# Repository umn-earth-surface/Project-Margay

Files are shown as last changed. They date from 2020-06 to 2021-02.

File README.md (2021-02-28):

# Project-Margay

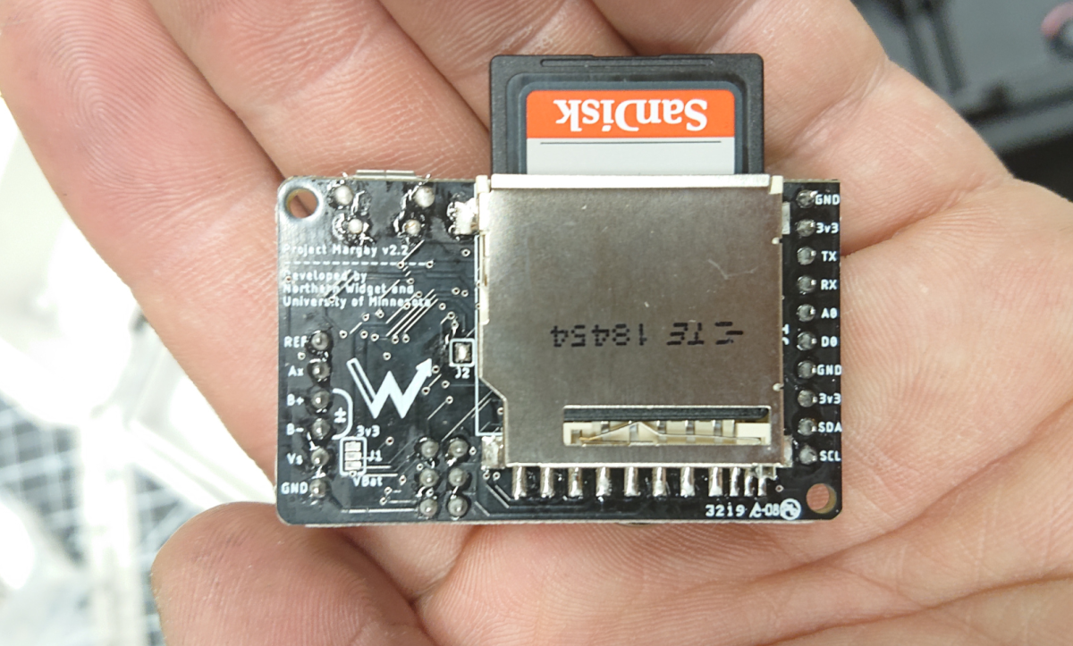
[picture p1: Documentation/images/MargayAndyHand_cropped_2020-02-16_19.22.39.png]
Margay Andy hand Dec 2020


***Margay data logger v2.2.*** *Back side with full-size SD card holder and pinout labels. Standard sized SD card for data storage and scale.*

Project Margay is a micro scale environmental data logger designed based on the ALog series, it is designed to trade IO capabilities for cost and size, allowing for a very simple, but very useful data logger

## Namesake

Due to its small size and adaptability to its environment, Project Margay takes its name from the small Margay cat native to the forests of South and Central America.

>> @awickert: Might be best to add in some feature abilities of the Margay datalogger in part of the namesake to mirror that of the Resnik - let me know what you think the highlights of the logger are and I'll (Josh) put them in

A margay, yawning

##Technical Specifications

>> @awickert: I'm (Josh) drafting up a couple of ways to display the technical specs better, no substantial changes at the moment, but it's next on my list

### Electronic Hardware
This includes a description of the PCB and component functionality

#### Features:
* ATMega644P Processor
* 3.3v Logic
* On board full size SD card (for ease of field use)
* Extremely low sleep current
* Input voltage designed for use with easy to find alkaline batteries
* 0.1" Pitch headers can be populated with header pins and placed on a breadboard for prototyping

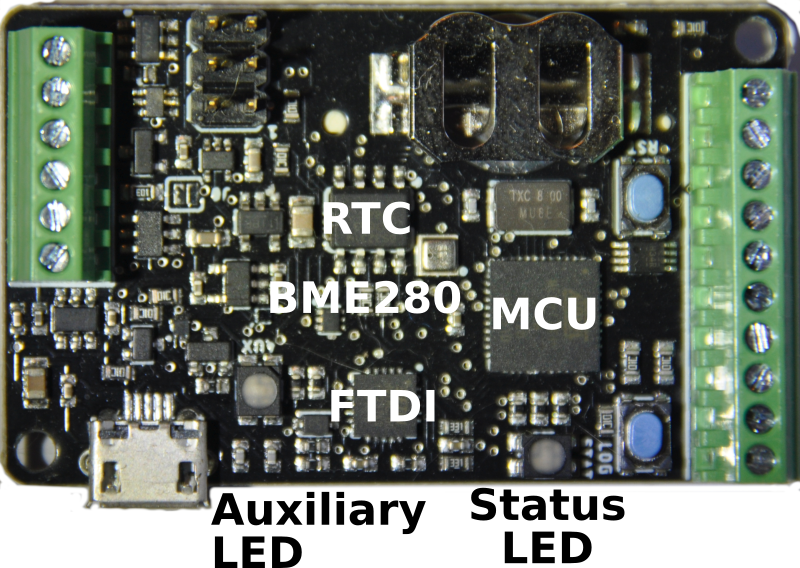
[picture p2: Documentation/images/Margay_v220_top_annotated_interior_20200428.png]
Margay v2.2 interior elements labeled


***Significant components on the Margay v2.2.***

#### v0.0 (Retired)
**Features** <br>
I<sub>Q</sub> = 1.6mA <br>
I<sub>out</sub> = 50mA, max (Regulated power supplied to sensors) <br>
V<sub>in</sub> = 3.3 ~ 5.5v <br>

**IO**:
* 1 I2C Bus
* 1 SPI Bus, with up to 2 CS pins
* 1 PWM Channel (output configurable to 3.3v or VBat via a jumper on bottom of board)
* RGB Status LED
* Auxiliary LED
* Reset Button
* Reconfigurable Button

#### v1.0
**Features** <br>
I<sub>Q</sub> = 2.5&mu;A <br>
I<sub>out</sub> = 50mA, max (Regulated power supplied to sensors) <br>
V<sub>in</sub> = 3.3 ~ 5.5v (Reverse polarity protected) <br>

**IO**
* 1 ADC, 18 bit
* 1 I<sup>2</sup>C Bus
* 1 SPI Bus, with up to 2 CS pins
* 1 PWM Channel (output configurable to 3.3v or VBat via a jumper on bottom of board)
* RGB Status LED
* Auxiliary LED
* Reset Button
* Reconfigurable Button

#### v2.0 (In development)
**Features** <br>
I<sub>Q</sub> = <2.5&mu;A (Estimated) <br>
I<sub>out</sub> = 200mA, max (Regulated power supplied to sensors) <br>
V<sub>in</sub> = 3.3 ~ 5.5v (Reverse polarity protected) <br>

**IO**
* 1 ADC, 18 bit
* 1 I<sup>2</sup>C Bus
* 1 UART Channel
* 2 GPIO Pins (one configurable as an 8 bit ADC)
* 1 PWM Channel (output configurable to 3.3v or VBat via a jumper on bottom of board)
* RGB Status LED
* Auxiliary LED
* Reset Button
* Reconfigurable Button

### Pinout and board interfaces
Pinout is listed on bottom of board, and shown here for v2.2.

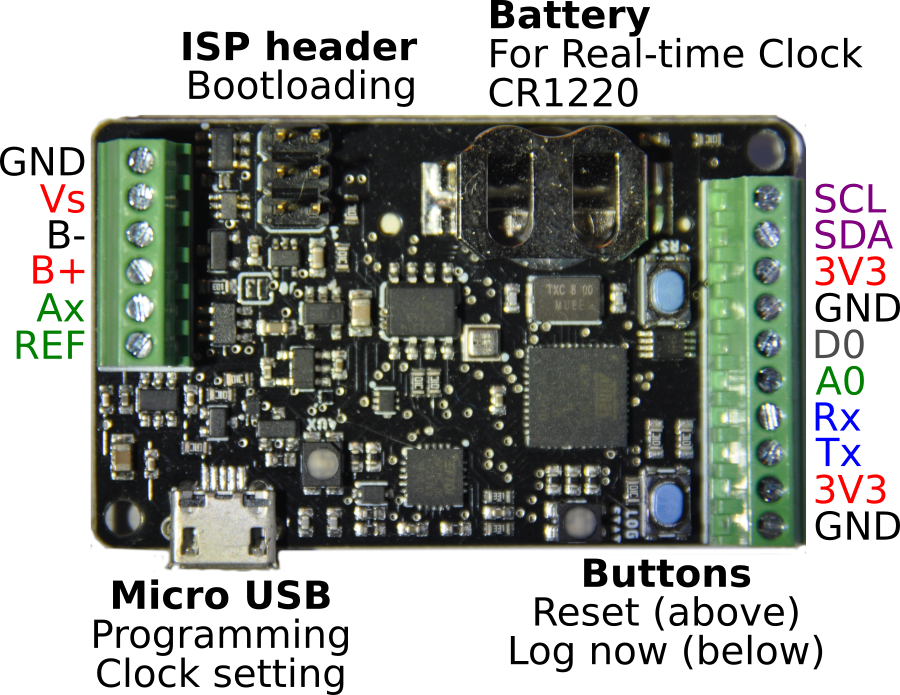
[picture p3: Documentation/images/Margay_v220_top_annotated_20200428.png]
Margay v2.2, top annotated


***Margay data logger, top annotated.***
* Positive voltage: red
* Ground: black
* Analog measurement system: green
* I2C bus: purple
* Digital I/O: gray
* UART (also called USART) bus: blue

*The jumper on the front of the board, to the right of "B+" and "Ax", connects an on-board reference resistor (10 kOhm in our builds) with the analog pin Ax to create a voltage divider in which the sensor between Ax and REF is on the GND side of the voltage divider.*

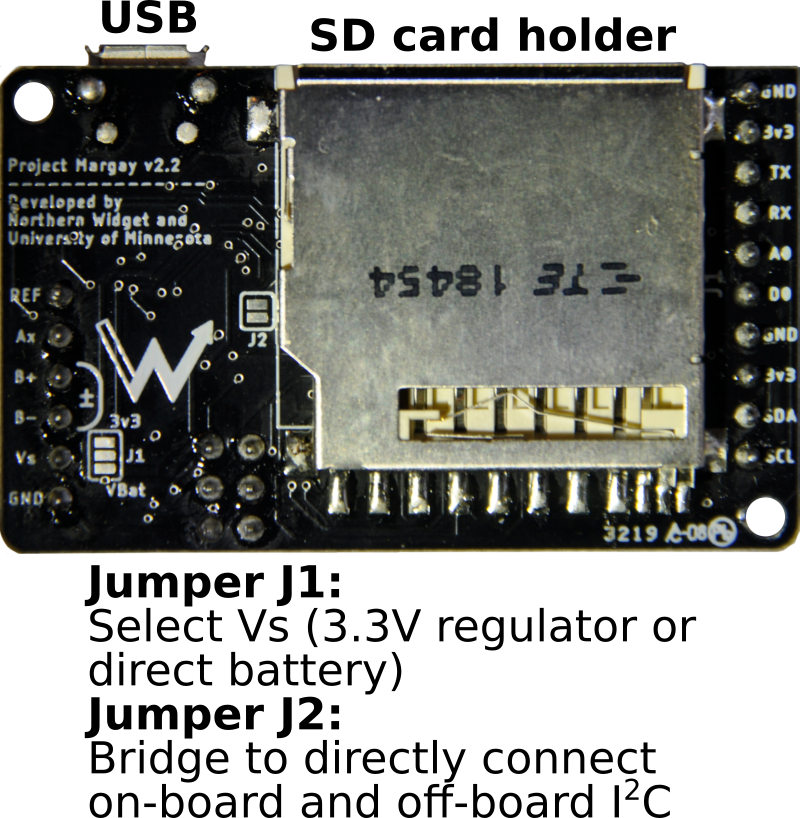
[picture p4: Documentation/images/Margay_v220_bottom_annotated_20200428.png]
Margay v2.2, bottom annotated


***Margay data logger, bottom annotated.*** This is where the labels for the above pins are printed.

In this pinout, the name of each pin is shown, as well as the group of pins which it belongs to, a detailed description of the pins and callouts follows:

#### Pins:
* 3v3, the switched 3.3v output rail, this rail can be turned on and off to disconnect power consumptive external devices
* GND, the main output ground
* BAT+, the positive connection for the battery line, voltage range 3.3v ~ 5.5v
* BAT-, Negative battery connection, this pin is NOT interchangeable with GND, as BAT- is reverse voltage protected to prevent damage from plugging the battery in backwards
* Vs, this is the switched PWM output, the voltage of this output is determined by a solder jumper on the bottom of the board, controlled by **D3**

* MOSI, this is the master out, slave in, pin for the SPI bus, which doubles as **D5** when SPI and SD card are not used
* MISO, this is the master in, slave out, pin for the SPI bus, which doubles as **D6** when SPI and SD card are not used
* SCK, this is the clock line for the SPI bus, which doubles as **D7** when SPI and SD card are not used
* CS, this is the chip select pin for the SPI bus, which doubles as both **D11** and **INT1** when external SPI is not used (Can be used even when SD card is used)

* SCL, this is the dedicated serial clock line for the I2C bus
* SDA, this is the dedicated serial data line for the I2C bus

#### Callouts:
1. This is the auxiliary LED, which indicate TX and RX status using red and blue channels, green channel is controlled by **D19**
2. This is the micro USB connection, which can be used for both programing via the Arduino IDE, and serial monitoring
3. This is the primary RGB status LED, where the individual channels are controlled by **D15**, **D14**, and **D13**
4. This is the reconfigurable push-button, generally used to initiate logging, it is read by **D2**, which is also **INT2**
5. This is the hardware reset button, which will force the micro to return to the initial state after code upload
6. This is the ICSP header, which can be used to burn the bootloader to the board or write programs to the chip without using the USB and bootloader

#### Onboard Pins:
Pin Name | Pin Number (v0.0) | Pin Number (v1.0) | Function
-------- | ----------------- | ----------------- | --------
`SD_CS` | D4 | D4 | Chip select pin on SD card
`SD_CD` | D1 | D1 | Card detection pin for SD card, active low, AUX power must be on to use
`BuiltInLED` | D19 | D20 | Connected to green channel on **AUX** LED, on when pin is low
`RedLED` | D13 | D13 | Connected to red channel on **STAT** LED, on when pin is low
`GreenLED` | D15 | D15 | Connected to green channel on **STAT** LED, on when pin is low
`BlueLED` | D14 | D14 | Connected to blue channel on **STAT** LED, on when pin is low
`VRef_Pin` | A2 | A2 | Analog pin to read 1.8v on board reference, AUX power must be on to use
`ThermSensePin` | A1 | A1 | Analog pin to read thermistor voltage divider, AUX power must be on to use
`BatSensePin` | A0 | A0 | Analog pin to read battery voltage divider, AUX power must be on to use
`VSwitch_Pin` | D3 | D3 | Connected to MOSFET driver for **Vs** pin, active low
`Ext3v3Ctrl` | D12 | D19 | Turns on AUX power, active low
`I2C_SW` | N/A | D12 | Switches between on board I2C and external I2C
`PG` | D18 | D18 | Power good pin from core 3v3, can be used to test if core 3v3 is stable, pulled low when power is not stable
`ExtInt` | D11 | D11 | External interrupt and external chip select pin
`RTCInt` | D10 | D10 | Interrupt (`INT0`) connected to RTC /INT line, active low
`LogInt` | D2 | D2 | Interrupt (`INT2`) connected to **LOG** button, active low

### Assembly

Assembling this data logger is possible by hand with sufficient skill and the following tools:
* Temperature-controlled soldering iron
* Hot-air rework station
* Equipment for stenciling with solder paste
* ESD-safe tweezers and workstation
* Solder wick

Mechanized assembly by a professional circuit-board assembly house, which is available in many parts of the world, may be preferred due to the complexity of this data logger board.

>> @awickert: I copy and pasted the same bit from the Resnik readme, let me (Josh) know if anything should be more specific/changed here - could also start work on that assembly guide mentioned in the Resnik readme comment after the Margay readme is more put together

### Electronic Software and Firmware

NOTE: Users should see the code included below in the README and follow the directions indicated in http://northernwidget.com/tutorial. Some of the below information is deprecated.

NOTE: Currently, users should modify their Arduino libraries to include the most recent version 1 of SdFat; Margay is incompatible at present with version 2.

>> @awickert: This section and the section below should be reorganized to mirror that of the Resnik readme, will get to it as soon as I (Josh) reorganize some of the previous info

## Using Northern Widget Software
This includes a usage guide to demo software which is provided to both test the hardware features of the board in general (the MargayHardwareTest file), and to set the device up as a logger using a [TP-Downhole](https://github.com/NorthernWidget/TP-DownHole) device as a sensor which runs on I2C. This logger demo tests all hardware on the board and ensures all required systems are connected and indicates the result of these tests using the Status LED on startup. A green light indicated all systems check out, and the device is ready to log, otherwise a red light indicates there is a problem, it is recommended to open up a serial monitor to determine which system is failing. If a green light is indicated, when the system is ready to log, logging is initiated by pressing the log button, which makes an initial log and starts a sequence of logs which will continue to occur every 15 minutes (by default) of by a different user defined time. In between logging events, the system is put to sleep to save power. Each time the log button is pressed, a new SD card file is created named "Logx.txt" where x increments with each button press, and each one of these individual files is initiated with a header to inform the user of the data columns used by the CSV type file.

To use this software the following libraries must be installed in the Arduino IDE:
* [SdFat](https://github.com/greiman/SdFat)
* [DS3231_Logger](https://github.com/NorthernWidget/DS3231_Logger)
* [MCP3421](https://github.com/NorthernWidget/MCP3421)
* [MS5803](https://github.com/NorthernWidget/MS5803)

Information on library instillation can be found on the [Arduino](https://www.arduino.cc/en/Guide/Libraries) site, the "Manual" instillation method should be used to ensure success

The Northern Widget board definitions will also be required, the Margay board should be run using the "TLog v1" board definition. Information on how to install and select a board definition can be found in the Northern Widget Board Definitions [readme](https://github.com/NorthernWidget/Arduino_Boards)

## Using Custom Software (Developer)
As we provide all information about on board pins and their functionality, it is easy for a user to write their own code in the Arduino IDE to leverage the hardware capabilities of the Margay to whatever degree is desired. To do this, the Northern Widget board file can be used (as described above), or the **[MightyCore](https://github.com/MCUdude/MightyCore)** Board files can be used. These are the board files the Northern Widget ones were based on, but allow for more compilation options for the user. Full instructions for instillation and use are provided on the MightyCore GitHub page.

For the Margay (any model), the recommended settings are as follows:

Setting | Value
--------|------
`Board` | `ATmega644`
`Pinout` | `Standard`
`Clock` | `8MHz External`
`Compiler LTO` | `Disabled`
`Variant` | `644P/644PA`
`BOD` | `2.7v`

# Sample code

`Margay_NoSensors.ino`

```c++
// Include the Walrus library
#include "Margay.h"
// Include any sensor libraries.
// The Northern Widget standard interface is demonstrated here.
//Sensor mySensor;

// Declare variables -- just as strings
String header;
String data;

// Instantiate classes
// Sensor mySensor (for any Northern Widget standard sensor library)
Margay Logger(Model_2v0, Build_B); // Margay v2.2; UPDATE CODE TO INDICATE THIS

// Empty header to start; will include sensor labels and information
String Header = "";

// I2CVals for sensors
// Add these for any sensors that you attach
// These are used in the I2C device check (for the warning light)
// But at the time of writing, the logger should still work without this.
uint8_t I2CVals[] = {};

//Number of seconds between readings
uint32_t updateRate = 60;

void setup(){
    Header = Header;//+ mySensor.getHeader();
    Logger.begin(I2CVals, sizeof(I2CVals), Header);
}

void loop(){
    Logger.Run(update, updateRate);
}

String update() {
    initialize();
    //return mySensor.getString(); // If there were a sensor attached
    return ""; // Empty string for this example: no sensors attached
}

void initialize(){
    //mySensor.begin(); // For any Northern Widget sensor
                        // Other libraries may have different standards
}
```

# Developer Notes

+ (**<= Mrk 1.0**) When using power from the external rail (the 3v3 on the screw terminals) it is always advised to have a battery connected to the board, even if connected via USB. The USB connection is able to power the core components, but not the external rail. We know this is annoying, but fear not, the Northern Widget team is [working tirelessly](https://i.imgur.com/Kx97N0l.gifv) to fix this for the Mrk 2.0!
+ (**<= Mrk 1.0**) When using I<sup>2</sup>C on the device, external pullups (4.7k&Omega; ~ 10k&Omega;) are required. If using device strictly onboard the internal pullups on the ATMEGA seem sufficient, but if you add capacitance of a cable attaching to an external sensor, etc, this is often too much, since the internal pullups are very weak. This is also being fixed in the Mrk 2.0 version with dedicated switchable on board pullups.
+ (**All models**) The external power rails and the switched battery rail should be enabled in hardware by default, however, it is our recommendation to explicitly define these pins (`Ext3v3Ctrl`) as outputs and drive them `LOW` even if you never intend to switch them on and off. This prevents the rails from inadvertently being turned off due to a transient on the floating control line.

## Acknowledgments

Support for this project provided by:

UMN ESCI

NSF

<br/>
<br/>
<br />This work is licensed under a <a rel="license" href="http://creativecommons.org/licenses/by-sa/4.0/">Creative Commons Attribution-ShareAlike 4.0 International License</a>.

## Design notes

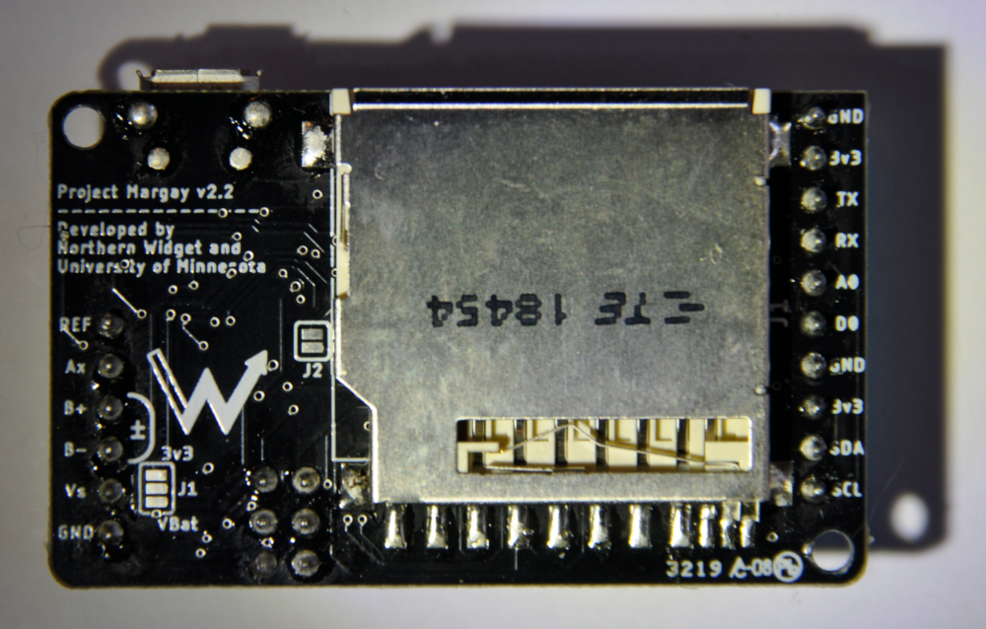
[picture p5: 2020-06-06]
Documentation/images/Margay_v220_back_with_shadow_20200428.png

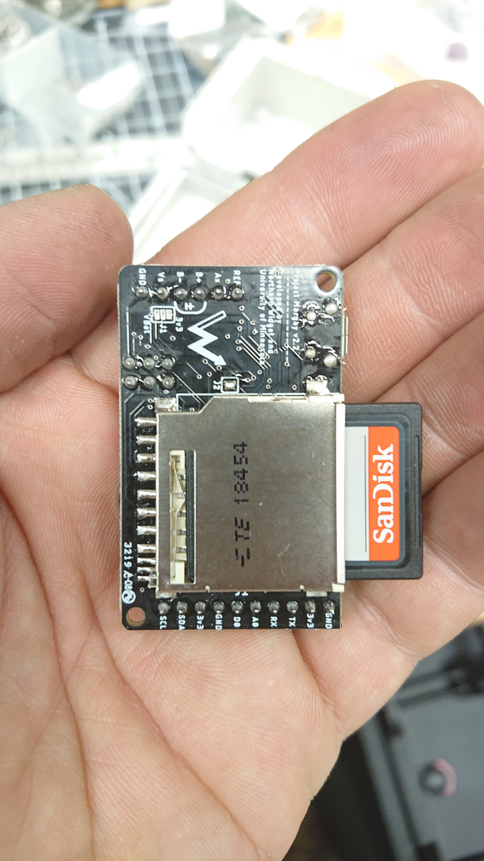
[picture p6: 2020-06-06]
Documentation/images/MargayAndyHand_2020-02-16_19.22.39.jpg

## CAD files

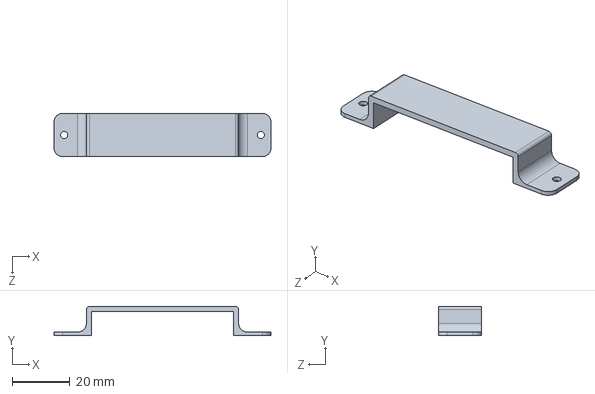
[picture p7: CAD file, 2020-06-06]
3Dprint/BatteryMount_Strap.SLDPRT
75.0 x 10.0 x 15.0 mm

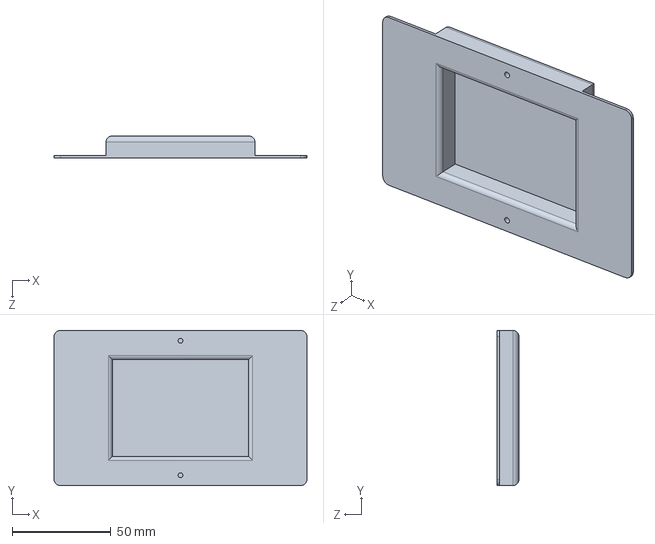
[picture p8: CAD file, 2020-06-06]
3Dprint/BatteryMount_WH10.SLDPRT
128.0 x 78.5 x 11.2 mm

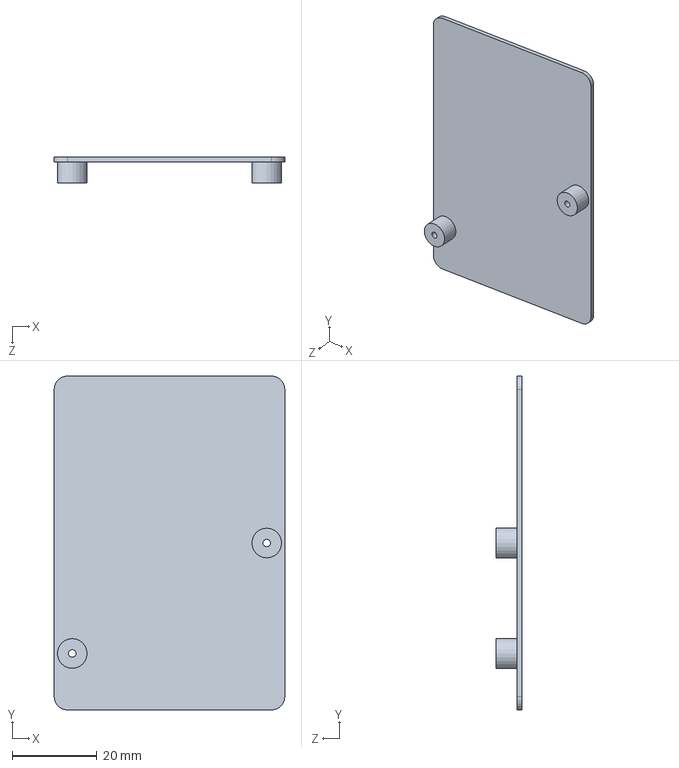
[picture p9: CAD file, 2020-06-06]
3Dprint/MargayMount_WH02_lid.SLDPRT
54.4 x 78.7 x 6.20 mm

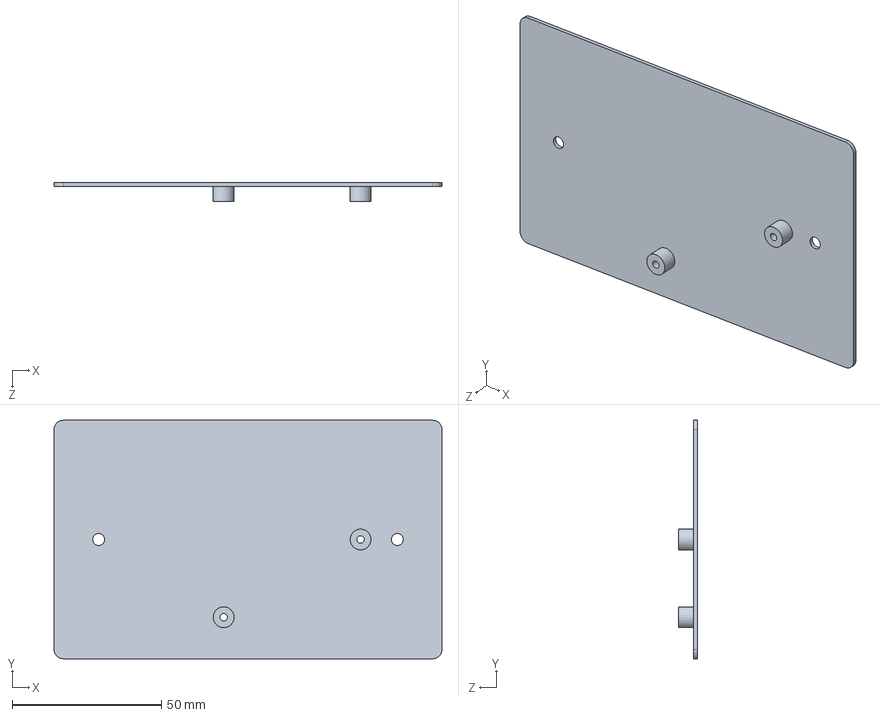
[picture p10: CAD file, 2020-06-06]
3Dprint/MargayMount_WH10.SLDPRT
129.9 x 79.9 x 6.20 mm

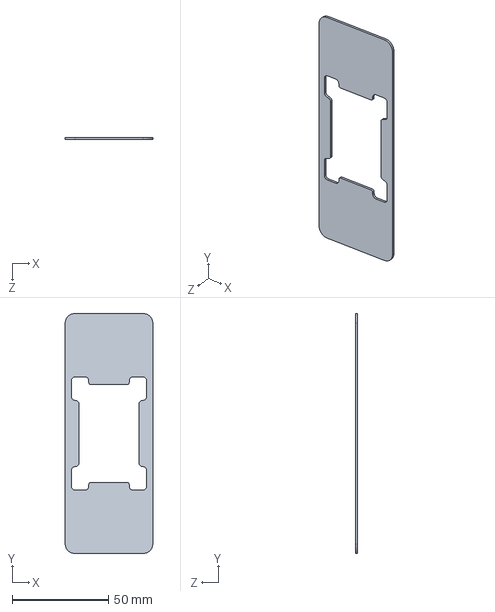
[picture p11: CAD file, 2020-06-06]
3Dprint/StencilMount_Margay.SLDPRT
45.5 x 124.4 x 1.20 mm

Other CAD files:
3Dprint/BatteryMount_Strap.STL
3Dprint/BatteryMount_WH10.STL
3Dprint/MargayMount_WH02_lid.STL
3Dprint/MargayMount_WH10.STL
3Dprint/StencilMount_Margay.STL

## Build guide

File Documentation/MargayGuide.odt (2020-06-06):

Margay Operations Guide

Initialize

1. Ensure that all connections are secure and SD card is inserted

2. Turn battery pack on

3. Wait for GREEN - GREEN - 5x Blue Flash.

- If you see this, the logger is properly recording data. To double-check, go to "Check".

- If you see a different flash pattern, go to "Error".

Check

1. After going through "Initialize", wait 2-3 minutes.

2. Follow the instructions in the "Download" section

3. Check to make sure that all the data are being recorded at the proper (UTC) time.

4. Check that valid values are being recorded for sensors.

7. Whether or not files are properly recorded, return to "Initialize"

- If files are not recorded, replace the SD card, check all connections, turn the logger back

on, and try again

- If there is an issue with a specific sensor, check connections and troubleshoot

- If files are recorded properly, return to Initilaize and do not return to "Check"

SD card swap

1. Turn battery pack off.

2. Remove SD card. Ensure that it is labeled. Put it somewhere safe and memorable.

3. Replace the SD card with an equivalently labeled SD card.

4. Go to "Initialize"

Download

1. Turn battery pack off.

2. Remove SD card.

3. Insert SD card in computer.

4. Navigate in the SD card to the most recent "log" file (NW→<serial_number>→Log<number>.txt).

5. Save the data file in a well-labeled and organized place.

6. Safely eject the SD card from the computer

7. Go to "Initialize"

Error

(Status Codes)

The first LED (AUX) will turn green so long as power is applied.

The second LED (STAT) will have one of the colors below.

Green: All systems check out OK, logging will proceed

Orange: A sensor system is not registering properly, some sensor data may be missing or incorrect

- Verify correct polarity of sensor connection
- Ensure the right sensor is connected
- Verify the screw terminals are well connected to the wires (a lose connection can cause a failure)
- Make sure battery power is applied, some sensors can fail otherwise

Cyan: Clock time is incorrect, but logger is otherwise working correctly

- Connect the logger to a computer and reset the clock using the Northern Widget Time Set GUI
  - Start Processing
  - Open the Northern Widget Time Set program
  - Note and record the wrong time if the logger has been out in the field, alongside the current (correct) time, to correct the prior measurements
  - Click the "set time" button and check that you are <3 seconds off of the correct time.
  - Click the "close" button.

Pink (looks like purple to some people): SD card is not inserted

- Insert the SD card, or remove and re-insert to make sure card is fully seated

Red: Critical on board component is not functioning correctly, such as SD card or clock. Logging will likely not be able to proceed

- Attempt power cycle
- Try different SD card
- Disconnect all sensors; reconnect one by one and check.

Yellow, Fast Blinking: <50% battery capacity.

- Replace batteries: turn battery pack off, replace batteries, and turn battery pack back on.

Red, Fast Blinking: Batteries <3.3V. Voltage too low to properly function.

- Replace batteries: turn battery pack off, replace batteries, and turn battery pack back on.

General tips to solve many kinds of errors

- Turn the the logger off and on
- Verify the quality of all screw terminal connections by gently tugging on the wires and making sure they stay in place, if not, remove, replace, and re-tighten the connection
- Ensure sensors and/or cables are not damaged, this can result is shorts or other problems
- Make sure batteries have sufficient voltage to run the logger (>3.3 V)
